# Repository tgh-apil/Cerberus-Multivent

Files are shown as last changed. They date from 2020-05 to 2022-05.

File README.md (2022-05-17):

# Cerberus-Multivent
A system using standard ventilation circuit parts and localy-manufacturable custom components to allow the use of a single ventilator to support multiple patients.

The system allows **independent control of tidal volume, FiO2, and PEEP for each patient**. 

The sub-circuit for each patient is pressure isolated and separated by N99 filters from main ventilator. There is no theoretical limit on the number of secondary circuits possible. The effective limitations are physical space for patients and the maximum tidal volume and pressure deliverable by the primary ventilator.

Supports pressure-limited volume control ventilation only. Patients must be deeply sedated with minimal spontaneous respitory activity.

Cerberus-Multivent is an open-source medical device project managed by the [Lynn and Arnold Irwin Advanced Perioperative Imaging Lab](https://apil.ca) at Toronto General Hospital, University Health Network.

# DISCLAIMER
This is an **INVESTIGATIONAL MEDICAL DEVICE** being evaluated for use
in hospital setting during **extreme crisis** leading to ventilator
shortages.

It has **not been approved** by any regulatory body.

Its use is **not endorsed** by any institution or professional body,
including the ones where it was developed and tested.

We have made every effort to make the system as safe as possible and to
provide documentation and educational materials for its use, should it be
necessary, in order to minimize the very significant risks of iatrogenic harm.

Any clinical application requires close monitoring of patients by automated 
systems and living, breathing care providers familiar with the system and its 
hazards.

It is posted here in order to facilitate rapid knowledge sharing and research
on strategies for addressing the global ventilator shortages.

Any of use of this device is done purely at your own risk and liability. The
developers and associated institutions do not accept any liability for its use.

# Publications & Media
1. <a href="https://journals.lww.com/ccejournal/Fulltext/2020/05000/Personalized_Ventilation_to_Multiple_Patients.3.aspx?context=LatestArticles" rel="nofollow" target="_blank">Han JS, Mashari A, Singh D, Dianti J, Goligher E, Long M, Ng W, Wasowicz M, Preiss D, Vesely A, Kacmarek R, Keshavjee S, Brochard L, Fisher JA, Slutsky AS. Personalized Ventilation to Multiple Patients Using a Single Ventilator: Description and Proof of Concept. Critical Care Explorations. 2020 May;2(5):e0118.</a>
2. <a href="https://www.cbc.ca/listen/live-radio/1-193-fresh-air/clip/15775663-how-a-doctor-used-his-mentors-30-year-old-paper-to-make-a-split-ventilator-for-two-people" rel="nofollow" target="_blank">How a doctor used his mentor’s 30-year-old paper to make a split ventilator for two people. Fresh Air with Nana aba Duncan. Toronto: Canadian Broadcasting Corporation; 2020.</a>

# Documentation
Cerberus was originally designed to allow complete assembly using commercial off-the-shelf (COTS) ventilator circuit components. In addition to this original version, we created two custom components to make the system more robust and allow the adjustment of PEEP for each patient. Custom component design files can be found in the repository.

## Bill of Materials & Assembly Instructions:

1. <a href="https://github.com/tgh-apil/Cerberus-Multivent/blob/master/Documentation/Cerberus%20-%20BOM%20and%20Assembly%20Instructions%20-%20Hospital%20COTS%20Components.pdf" rel="nofollow" target="_blank">BOM and Assembly Instructions (COTS version)</a>

2. <a href="https://github.com/tgh-apil/Cerberus-Multivent/blob/master/Documentation/Cerberus%20-%20BOM%20and%20Assembly%20Instructions%20-%20Micromanufactured%20Components.pdf" rel="nofollow" target="_blank">BOM and Assembly Instructions (With customized components)</a>

## Instructions for Use

1. <a href="https://github.com/tgh-apil/Cerberus-Multivent/blob/master/Documentation/Cerberus%20-%20Safety%20Check%20Lists.pdf" rel="nofollow" target="_blank">Safety Check Lists</a> 

2. <a href="https://github.com/tgh-apil/Cerberus-Multivent/blob/master/Documentation/Cerberus%20-%20Quick%20Guide.pdf" rel="nofollow" target="_blank">Quick Guide</a> 

## Mathematical Model & Simulator

A mathematical model of the system along with a simulator have been created for staff training. The simulator includes a solver that suggests settings to achieve specific end points. All software is in beta. Software is for educational and research use only.

1. <a href="https://github.com/tgh-apil/Cerberus-Multivent/tree/master/Simulator" rel="nofollow" target="_blank">Mathematical Model</a>

2. <a href="https://ventilator-simulator.now.sh/" rel="nofollow" target="_blank">Simulator</a>  

Developed by Azad Mashari, Eitan Grinspun, Bai Li, Isaac Waller, Jim Duffin, Devin Singh

# Cerberus-multivent: System Description

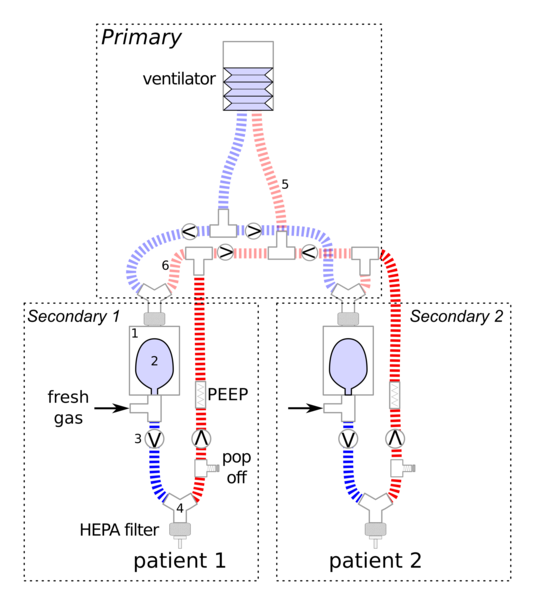
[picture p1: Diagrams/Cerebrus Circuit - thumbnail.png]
Cerberus Schematic


One suggested approach to the severe global shortage of ventilators during the current pandemic has been the splitting of ventilators in order to ventilate multiple patients with one device. The simplest version of this involves simply splitting the inspiratory and expiratory limbs of the circuit into a branch for each patient. Indeed a 3D-printable splitter device, the Prisma VEsper, was granted emergency approval by the FDA last week. This approach however poses significant risks and has a high likelihood of harming one or both patients. This motivated a joint statement by all the major critical
care and related societies (<a href="https://www.apsf.org/news-updates/joint-statement-on-multiple-patients-per-ventilator" rel="nofollow" target="_blank">https://www.apsf.org/news-updates/joint-statement-on-multiple-patients-per-ventilator</a>) warning about the hazards of such an approach.

Cerberus, named for the multi-headed dog of Greek mythology, is a ventilator splitting system that allows largely independent ventilation settings for the co-ventilated patients.

The primary ventilator works to drive multiple bellows assemblies, one for each patient. Each patient has a separate fresh gas flows and pressure-isolated secondary circuit.

On inspiration, the inspiratory pressure generated by the ventilator is Y split with one arm per patient. The gas flow from each of these arms drives a bellows assembly (consisting of reservoir bag inside a canister) uniquely connected to the inspiratory limb of each patient circuit. These also include fresh gas inlets for each patient. There is no sharing of inspiratory gas streams. Each patient receives customized fresh gas mix from an unshared source. During expiration the fresh gas flow refills the reservoir bag for the next breath. The expiratory limbs for each patient include an in-line PEEP valve and converge, along with the drive gas outflow from the bellows assemblies into the expiratory limb of the primary circuit. Check valves and filers are placed to pressure isolate all patient circuits and mitigate risk of infections transmission among patients.

# Development Team &amp; Collaborators

The Cerberus multi-vent is based on a design first presented by Sommer, Fisher et al. **Sommer DD, Fisher JA, Ramcharan V, Marshall S, Vidic DM. Improvised automatic lung ventilation for unanticipated emergencies. Crit Care Med. 1994;22: 705–709.** You can find a personal account from Dr. Joe Fisher of how the project came about <a href="https://www.drjoefisher.com/posts/fresh-air-cbc-may-9-2020-covid-19-and-the-real-back-story" rel="nofollow" target="_blank">here</a> 

**Core Development Team**: Jay Han, Devin Singh, Joseph Fisher, and Azad Mashari, From the Department of Anesthesia and Pain Management, Toronto General Hospital, University Health Network.

**Review & Evaluation**: Jose Dianti, Ewan Goligher, Michael Long, William Ng, Marcin Wasowicz, David Priess, Alex Vesely, Arnaud Mbadjeu, Robert Kacmarek, Shaf Keshavjee, Maha Al-Mandhari, Jesse May, Laurent Brochard, and Arthur Slutsky, from the Departments of Anesthesiology and Pain Management, Critical Care Medicine, Respiratory Care, Surgery and Medicine at University Health Network & St. Michaels Hospital, Toronto; Hospital Italiano de Buenos Aires, Argentina; Brigham and Women’s Hospital, Boston; Surrey Memorial Hospital, Surrey. 

Development was supported by grants from the **University Health Network & Sinai Health Systems Academic Medical Organization COVID-19 Innovation Fund** and the **Toronto General & Western Hospital Foundation** at the University Health Network. This work would not have been possible without the logistical support and hundreds of hours of work from numerous collaborators including:

**UHN Medical Engineering**: Maciej Bauer, Gad Acosta, Dave Gretzinger, Ewaryst Kulikowski, Katina DiBiase

**University of Toronto Engineering / Toronto Tool Library Collaboration**: Kate Kazlovich, James Wallace, Marc Shu-Lutman, Kyle Mayers, Simon Lynch 

**UHN Department of Anesthesia and Pain Management**: Jo Carroll, Samareh Ajami

**UHN/Peter Munk Cardiac Centre,
 Lynn and Arnold Irwin Advanced Perioperative Imaging Lab**: Joshua Qua Hiansen, Vahid Anwari

**Techna Institute**: Jimmy Qiu and Team

**UHN Animal Lab**: Badru Moloo, Alyssa Goldstein, Beth Pielsticker, Sandra Lafrance and Team

**UHN Healthcare Human Factors**: Joe Cafazzo, Neil Sokol, Wayne Ho, Julie Malone

**University of Toronto Computer Science**: U of T CS Department: Eitan Grinspun, Bai Li, Isaac Waller

**UHN Infection Prevention and Control and Medical Device Reporcessing**: AnnMarie Tyson, Kathleen Ross, Alon Vaisman, Kevin Wan

**UHN Foundation**: Shauna Seabrook

**UHN Public Affairs**: Rosa Kim

Thank you!

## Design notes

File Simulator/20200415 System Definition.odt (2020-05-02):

Cerberus Simulator System Definition

2020 April 14

Note: all pressure values are gauge readings referenced to 1 atm = 0

X[i] indicated patient specific parameter X for each of two patients on the system

# 1. INPUTS

## 1.1. Patient characteristics (for each of two patients)

1.1.1. Height (H[i]): 110-200 cm

1.1.2. Weight (W[i]): 40-120 kg

1.1.3. Lung Compliance (Cr[i]): 10-70 ml/cmH20 (intervals of 5)

1.1.4. Ratio of arterial partial pressure of oxygen to fraction of inspired oxygen (PF[i]): range 100 (severe dysfunction) - 500 (Normal)

For simplicity we are combining a whole bunch of physiological parameters into one.

## 1.2. Ventilator settings

### 1. 2.1. Primary ventilator settings

1.2.1.1. Pressure Control Level (PC) : 0-70 cmH20 (intervals of 5)

1.2.1.2. Positive End-Expiratory Pressure Level (PEEP0): Should always be set to 0 and somehow *gently* highlighted. Setting this above zero is a common error.

1.2.1.3. Respiratory Rate (RR): 2-40 breaths/minute

1.2.1.4. Inspiratory Time (IT): 0.5-(0.6/RR) s (That is inspiration should be no more than 60% of the respiratory cycle)

1.2.1.5. Inspiratory Time:Expiratory Time Ratio (IER): Discrete: 1.5:1 ; 1:1 ; 1:2 ; 1:3 (This represents the same info at IT but in a different form that will be more familiar for some users. For simplicity we can make this adjustable and make IT automatically calculated and displayed next to it. [ I:E = IT:((1/RR)-IT) ]

### 1.2.2. Secondary circuits settings (for each of two secondary circuits

1.2.2.1. Fresh Gas Oxygen Flow (FGFO[i]): 0-15 LPM (intervals of 1 for all flow variables)

1.2.2.2. Fresh Gas Air Flow (FGFA[i]): 0-15LPM

1.2.2.3. PEEP Valve Setting (PEEP[i]): 0-25 cmH20

# 2. Outputs

(values outside normal range should be highlighted)

## 2.1. Patient Arterial Blood Gas Analysis (for each patient)

2.1.1. pH[i]: Normal 7.3-7.4. Function of PaCO2[i] and HCO3[i];

- [H+] nM/L = 24 * PaCO2 (mmHg)/[HCO3] mM/L
- pH = -log10[H+]

2.1.2. Partial pressure of carbon dioxide (PaCO2[i]): N 35-45 mmHg (note different pressure units from above pressure values)

- Function of minute alveolar ventilation (3.1) and CO2 Production (3.2).
- We can assume that expired gas has similar CO2 partial pressure to the arterial gas, so
- MAV[i]*PaCO2[i] = CO2P[i] (unit conversions needed)

2.1.3. Partial pressure of oxygen (PaO2[i]): N > 100 mmHg PO2 = FiO2 * PaO2:FiO2

2.1.4. Bicarbonate concentration (HCO3[i]): N 22-28 mEq/L

## 2.2. Ventilator derived values (for each patient)

2.2.1. Peak Inspiratory pressure (PIP[i]): range 0-40 cm H2O; note: circuit includes a pop-off valve at 40 so pressure can never go above that

2.2.2. Actual PEEP (APEEP[i]): cm H2O

- Total fresh gas flow: FGFTot[i] = FGFO[i] + FGFA[i] (air + oxygen)
- Intrinsic PEEP (from FGF): PEEPInt[i] = 0 if FGFtot[i] < 7LPM; 3 + (FGFtot[i] – 7)*0.6
- APEEP[i] = PEEP0 + PEEPInt[i] + PEEP[i]

2.2.3. Tidal volume (VT[i]): 50-700 ml (Normal range depends on weight: 4-8 ml/kg) = 0.5x PIP x Cr for each patient (mean inspiratory pressure assumed to be half of PIP)

2.2.4. Fraction Inspired Oxygen (FiO2[i]): (FGFA*0.21 + FGFO) / (FGFA + FGFO)

# 3. Hidden Variables

## 3.1 Minute alveolar ventilation

3.1.1 Anatomical Dead Space ADS[i] = W[i]/0.45 ml

3.1.2 Secondary Circuit compliance CC[i] = constat CC for simplicity

3.1.3 Alveolar Tidal Volume AVT[i] = VT[i] – ( PIP[i] / 2*CC ) - ADS[i]

approx. assumes linear increase in pressure

3.1.4 Minute Alveolar Ventilation MAV[i] = RR*AVT[i]

3.2 CO2 production rate (VCO2[i]) = 0.4 + (Weight kg / 70 kg ) * 0.2 g / min (I more or less made this up; average value for 70kg adult is around 0.6 g/min and it varies with weight; for our purposes and the range of adult weights, we are considering that equation is probably good enough

# References

Kassirer JP, Bleich HL. Rapid Estimation of Plasma Carbon Dioxide Tension from pH and Total Carbon Dioxide Content. New England Journal of Medicine. 1965;272: 1067–1068. doi:10.1056/NEJM196505202722007 (https://doi.org/10.1056/NEJM196505202722007)

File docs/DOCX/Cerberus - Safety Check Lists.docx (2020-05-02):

Step 1: Driving Circuit Leak Test
Setup: a) Connect the inspiratory and expiratory limbs of the Cerebrus system to the corresponding inspiratory and expiratory ports of the driving ventilator b) Occlude the patient Y of each secondary circuit | Performance: I. Perform a standard low P leak test using an anesthetic gas machine | PASS - Leak < 500 mL

Step 2: Secondary Circuit Leak Test
Setup: a) Connect test lungs to the end of each secondary circuit* b) Set driving ventilator to initial system setup up parameters c) Begin ventilation on test lungs * Anesthetic gas machine (AGM) breathing bags can be used as test lungs* | Performance I. Allow the test lungs inflate and deflate II. Allow 2 minutes of ventilation III. Note the total volume returned to the ventilator IV. Allow the lungs to ventilate for an additional 2 minutes | PASS - Each test lung visually inflates and deflates with each respiratory cycle of the driving ventilator - Volume return to the ventilator remains constant for 2 minutes after the total volume was noted

Step 3: Fresh Gas Flow Check
Setup: a) Ensure the fresh gas flows to each secondary circuit is attached b) Set each fresh gas flow to 4 L/min | Performance I. With each fresh gas flow set to 4 L/min allow 2 minutes of ventilation II. After 2 minutes note the total volume returned to the ventilator III. Change the fresh gas flow on Lung A to 10 L/min while holding lung B at 4 L/min IV. Ventilate for 2 minutes V. Note the total volume returned to the ventilator VI. Note any change in the observed inflation in Lung A VII. Return fresh gas flow on Lung A to 4 L/min VIII. Repeat steps (III – VII) with lung B set to 10 L/min and lung A held at 4 L/min | PASS (all conditions must be met) - breath-delivery bag inflates and deflates with each respiratory cycle of the driving ventilator - Increased volume returned to driving ventilator AND increased lung expansion of Lung A following Step VI - Increased volume returned to driving ventilator AND increased lung inflation of Lung B following Step VIII

Step 4: Secondary Circuit Independence
Setup: a) Set driving ventilator to initial system setup up parameters b) Set fresh gas flow to 4 L/min c) Begin ventilation on test lungs | Performance: I. Allow system to ventilate for 2 minutes II. Measure the tidal volume or visually observe the approximate inflation of each lung III. Decrease the compliance in Lung A IV. Ventilate for 1 min V. Measure the tidal volume lung B or visually observe the approximate inflation of Lung B VI. Return the compliance of Lung A to baseline VII. Repeat steps (III – VI) using Lung B | PASS - No major changes in measured tidal volume or observed inflation of lung B when lung A compliance is decreased AND - No major changes in measured tidal volumes or observed inflation of lung A when lung B compliance is decreased

Step 5: Manometer Check
Setup: a) Set driving ventilator to initial system setup parameters b) Ensure manometer is installed into the sampling port of the HME filter distal to the patient Y c) Ensure each secondary circuit is attached to a test lung d) Ensure the PEEP valves on each secondary expiratory limb is set to 5 cm H2O e) Set fresh gas flow rates for each secondary circuit is set to 4 L/min | Performance: I. Note the nadir (lowest reading) on the manometer II. Note the zenith (highest reading) on the manometer | PASS - Zenith (peak inspiratory pressure) occurs with each inspiration - Peak inspiratory pressure does not equal the driving pressure of the ventilator - Nadir occurs at end expiration (PEEP) and the manometer reads at least 5 cm H2O* *PEEP may be higher than 5 cm H2O due to intrinsic PEEP generated by the constant fresh gas flow. Higher fresh gas flow rates lead to higher intrinsic PEEP*

Step 6: Disconnect Alarm
Setup: a) Set driving ventilator to initial system setup up parameters b) Set fresh gas flow to 4 L/min for each secondary circuit c) Begin ventilation on test lungs | Performance: I. Allow lungs to ventilate for 2 minutes to reach steady state II. Set volume alarms according to instructions on ALARM SETTING III. Disconnect Lung A IV. Reconnect Lung A V. Disconnect Lung B VI. Reconnect Lung B | PASS - Disconnect of Lung A results in low volume alarm AND - Disconnect of Lung B results in low volume alarm

Step 7: Pop-Off Valve Integrity AND Occlusion Alarm
Setup: a) Set driving ventilator to initial system setup up parameters b) Set fresh gas flow to 8 L/min for each secondary circuit c) Begin ventilation on test lungs | Performance: I. Allow lungs to ventilate for 2 minutes to reach steady state II. Set volume alarms according to instructions on “Alarm Settings” III. Clamp Lung A distal to secondary circuit Y IV. Note peak pressure on Lung A as measured by inline manometer V. Unclamp Lung A VI. Allow lungs to ventilate until volume alarm ceases VII. Clamp Lung B distal to secondary circuit Y VIII. Note peak pressure on Lung B as measured by inline manometer IX. Unclamp Lung A X. Allow lungs to ventilate until volume alarm ceases | PASS - Clamping of Lung A results in: - Low volume alarm - Peak inspiratory pressure as measured by inline manometer = 45 cm H2O AND - Clamping of Lung B results in: - Low volume alarm - Peak inspiratory pressure as measured by inline manometer = 45 cm H2O

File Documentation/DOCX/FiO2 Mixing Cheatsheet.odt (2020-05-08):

Total Flow (L/min) | 100% Oxygen (L/min) | Medical air (L/min) | FiO2
4 | 4 | 0 | 1.00
| 3 | 1 | 0.80
| 2 | 2 | 0.61
| 1 | 3 | 0.41
| 0 | 4 | 0.21
5 | 5 | 0 | 1.00
| 4 | 1 | 0.84
| 3 | 2 | 0.68
| 2 | 3 | 0.53
| 1 | 4 | 0.37
| 0 | 5 | 0.21
6 | 6 | 0 | 1.00
| 5 | 1 | 0.87
| 4 | 2 | 0.74
| 3 | 3 | 0.61
| 2 | 4 | 0.47
| 1 | 5 | 0.34
| 0 | 6 | 0.21
7 | 7 | 0 | 1.00
| 6 | 1 | 0.89
| 5 | 2 | 0.77
| 4 | 3 | 0.66
| 3 | 4 | 0.55
| 2 | 5 | 0.44
| 1 | 6 | 0.32
| 0 | 7 | 0.21
8 | 8 | 0 | 1.00
| 7 | 1 | 0.90
| 6 | 2 | 0.80
| 5 | 3 | 0.70
| 4 | 4 | 0.61
| 3 | 5 | 0.51
| 2 | 6 | 0.41
| 1 | 7 | 0.31
| 0 | 8 | 0.21
9 | 9 | 0 | 1.00
| 8 | 1 | 0.91
| 7 | 2 | 0.82
| 6 | 3 | 0.74
| 5 | 4 | 0.65
| 4 | 5 | 0.56
| 3 | 6 | 0.47
| 2 | 7 | 0.39
| 1 | 8 | 0.30
| 0 | 9 | 0.21

Total Flow (L/min) | 100% Oxygen (L/min) | Medical air (L/min) | FiO2
10 | 10 | 0 | 1.00
| 9 | 1 | 0.92
| 8 | 2 | 0.84
| 7 | 3 | 0.76
| 6 | 4 | 0.68
| 5 | 5 | 0.61
| 4 | 6 | 0.53
| 3 | 7 | 0.45
| 2 | 8 | 0.37
| 1 | 9 | 0.29
| 0 | 10 | 0.21
11 | 11 | 0 | 1.00
| 10 | 1 | 0.93
| 9 | 2 | 0.86
| 8 | 3 | 0.78
| 7 | 4 | 0.71
| 6 | 5 | 0.64
| 5 | 6 | 0.57
| 4 | 7 | 0.50
| 3 | 8 | 0.43
| 2 | 9 | 0.35
| 1 | 10 | 0.28
| 0 | 11 | 0.21
12 | 12 | 0 | 1.00
| 11 | 1 | 0.93
| 10 | 2 | 0.87
| 9 | 3 | 0.80
| 8 | 4 | 0.74
| 7 | 5 | 0.67
| 6 | 6 | 0.61
| 5 | 7 | 0.54
| 4 | 8 | 0.47
| 3 | 9 | 0.41
| 2 | 10 | 0.34
| 1 | 11 | 0.28
| 0 | 12 | 0.21

Total Flow (L/min) | 100% Oxygen (L/min) | Medical air (L/min) | FiO2
13 | 13 | 0 | 1.00
| 12 | 1 | 0.94
| 11 | 2 | 0.88
| 10 | 3 | 0.82
| 9 | 4 | 0.76
| 8 | 5 | 0.70
| 7 | 6 | 0.64
| 6 | 7 | 0.57
| 5 | 8 | 0.51
| 4 | 9 | 0.45
| 3 | 10 | 0.39
| 2 | 11 | 0.33
| 1 | 12 | 0.27
| 0 | 13 | 0.21
14 | 14 | 0 | 1.00
| 13 | 1 | 0.94
| 12 | 2 | 0.89
| 11 | 3 | 0.83
| 10 | 4 | 0.77
| 9 | 5 | 0.72
| 8 | 6 | 0.66
| 7 | 7 | 0.61
| 6 | 8 | 0.55
| 5 | 9 | 0.49
| 4 | 10 | 0.44
| 3 | 11 | 0.38
| 2 | 12 | 0.32
| 1 | 13 | 0.27
| 0 | 14 | 0.21

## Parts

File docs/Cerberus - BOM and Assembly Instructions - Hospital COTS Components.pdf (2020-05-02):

Equipment and Supplies (needed to prepare vent sharing between TWO (2) patients) Specific equipment required may vary depending on supplies and equipment availability

### 1. One (1) ventilator (driving ventilator) 2. Two (2) sets of patient tubing (inspiratory = blue, expiratory = white) 3. Four (4) short circuit tubings

a. Ideally two (2) pairs of distinctly different tubing colours (two (2) clear tubings and two (2) blue tubings)

### 4. Four (4) t-piece connectors (often used in spontaneous breathing trials) 5. Eight (8) 22 mm to 22 mm connectors 6. Six (6) 15 mm to 15 mm connectors

7. Four (4) y-connectors (normally used for connection of patient endotracheal tube to ventilator)

### 8. Eight (8) one-way valves (to be connected in-line) 9. Two (2) 1.5-2 L suction cannisters with corresponding lids

a. Cannister requirements
i. Lids must have at least two (2) communicating openings.
- One port must be able to connect the single end of a standard Y-connector to the cannister
- One port must be able to connect both the standard ventilator tubing on the external side of the lid and the breathing bag on the internal side of the cannister lid.
- This port must have a smaller secondary port on the external side of the cannister lid capable of connecting fresh gas supply
b. Ideally, the lid closes onto cannister with threaded connection. This cannister is pressurized and the lid must be prevented from leaking or being lifted up. If press fit, the lids must also be glued to the cannister. Glue (methyl methacrylate) can be used as gas from the cannister does NOT reach the patient.
10. Two (2) 1 litre anesthesia breathing bags (used to ventilate patients in circle system ventilators)

### 11. Two (2) silicone connectors 12. Two (2) Gas Sample Tee adapters 13. Two (2) 11.0 mm endotracheal tube (ETT) connectors

a. Can be found on 41 Fr Mallinckrodt double lumen ETT

### 14. Two (2) antimicrobial / heat and moisture exchangers (HMEs) 15. Two (2) elbow connectors (optional) 16. Two (2) manometers 17. Two (2) fresh gas flow lines

Note: Combined HME + antimicrobial filters are recommended if available. If unavailable, then one could use separate antimicrobial and HME filters. The filter must be placed between the patient Y and the ETT tube in order to filter the gas that is both inspired to and expired from the patient.

Images of required equipment

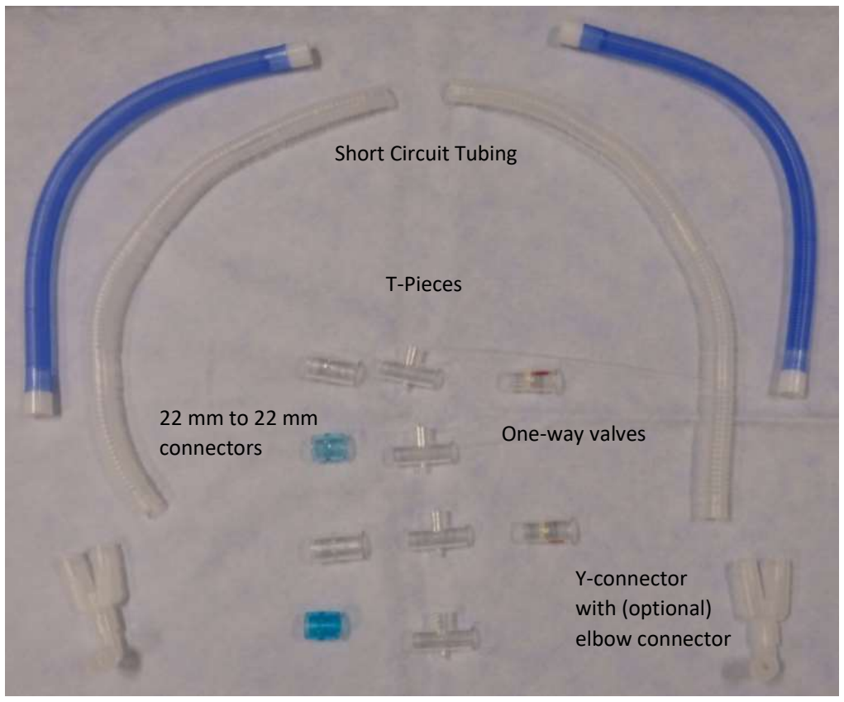
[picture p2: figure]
Short Circuit Tubing; T-Pieces; 22 mm to 22 mm connectors; One-way valves; Y-connector with (optional) elbow connector

### 2 L suction

cannister
and lid

Silicone
Connector

Breathing Bag 15 mm to 15 mm connector

Gas Sample Tee
adapters

ETT
connector

HME +
Antimicrobial
filter

PEEP valve
with connector
(2 options)

Patient Tubing

Manometer

### Cerberus System Schematic

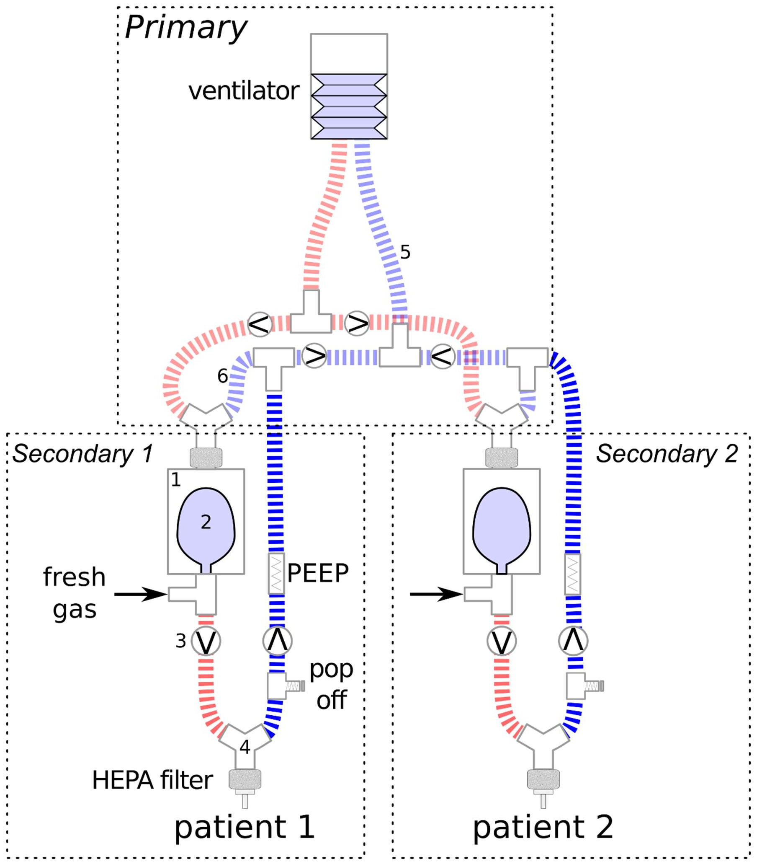
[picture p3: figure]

### Setting up the ventilator for two-patient ventilation

Creation of the “Driving Circuits”
Step 1: | Connect 22 mm to 22 mm connector (blue) to bottom of one (1) t-piece

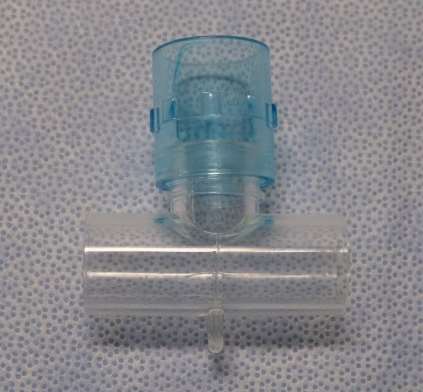
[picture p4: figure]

Step 2: | Connect short blue tubing to each open end of t-piece. This becomes the common inspiratory limb split of the ventilator (Master).

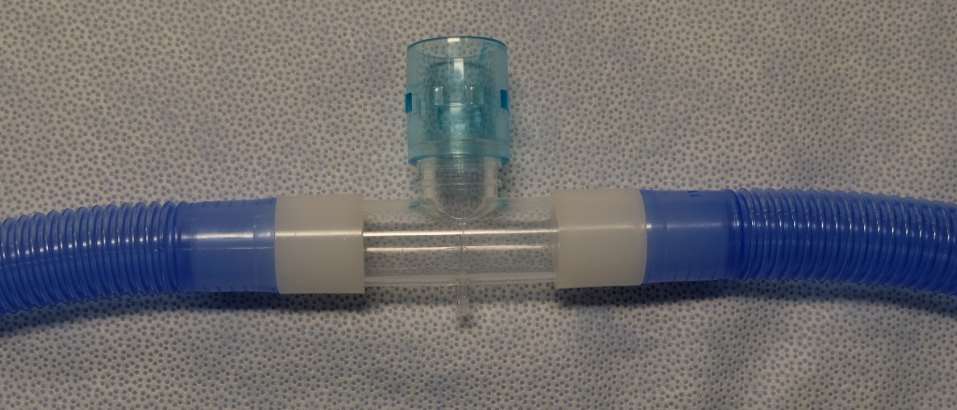
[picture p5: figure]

Step 3: | Connect the inspiratory limb t-piece (Step 2) to the common inspiratory port of the ventilator (Master) using the 22 mm to 22 mm connector previously attached (step 1) to the bottom of the t-piece.

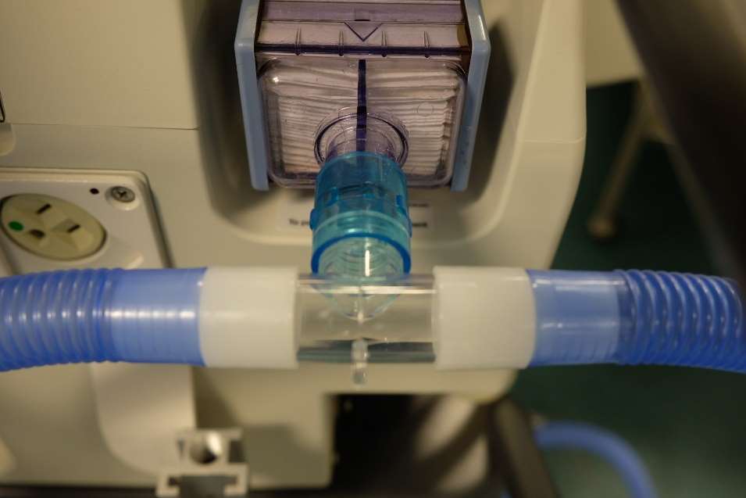
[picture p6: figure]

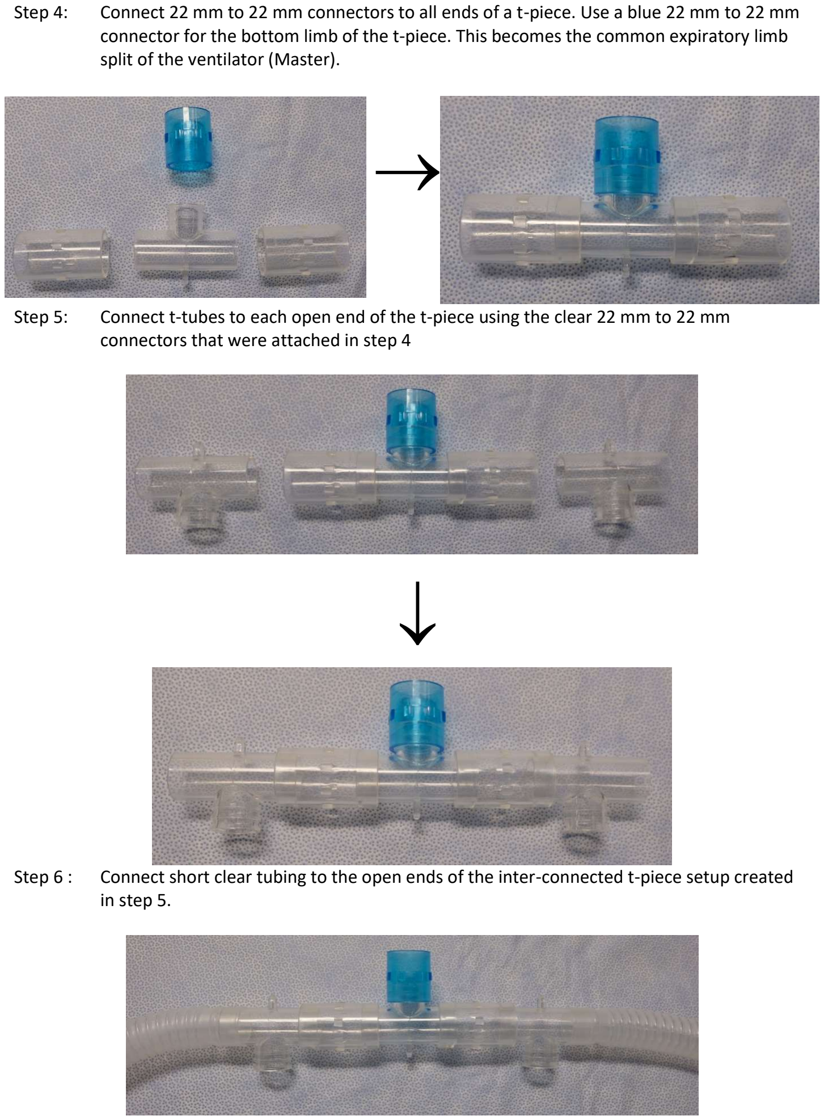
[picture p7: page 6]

Step 4: | Connect 22 mm to 22 mm connectors to all ends of a t-piece. Use a blue 22 mm to 22 mm connector for the bottom limb of the t-piece. This becomes the common expiratory limb split of the ventilator (Master).
Step 5: | Connect t-tubes to each open end of the t-piece using the clear 22 mm to 22 mm connectors that were attached in step 4
Step 6 : Connect short clear tubing to the open ends of the inter-connected t-piece setup created in step 5.

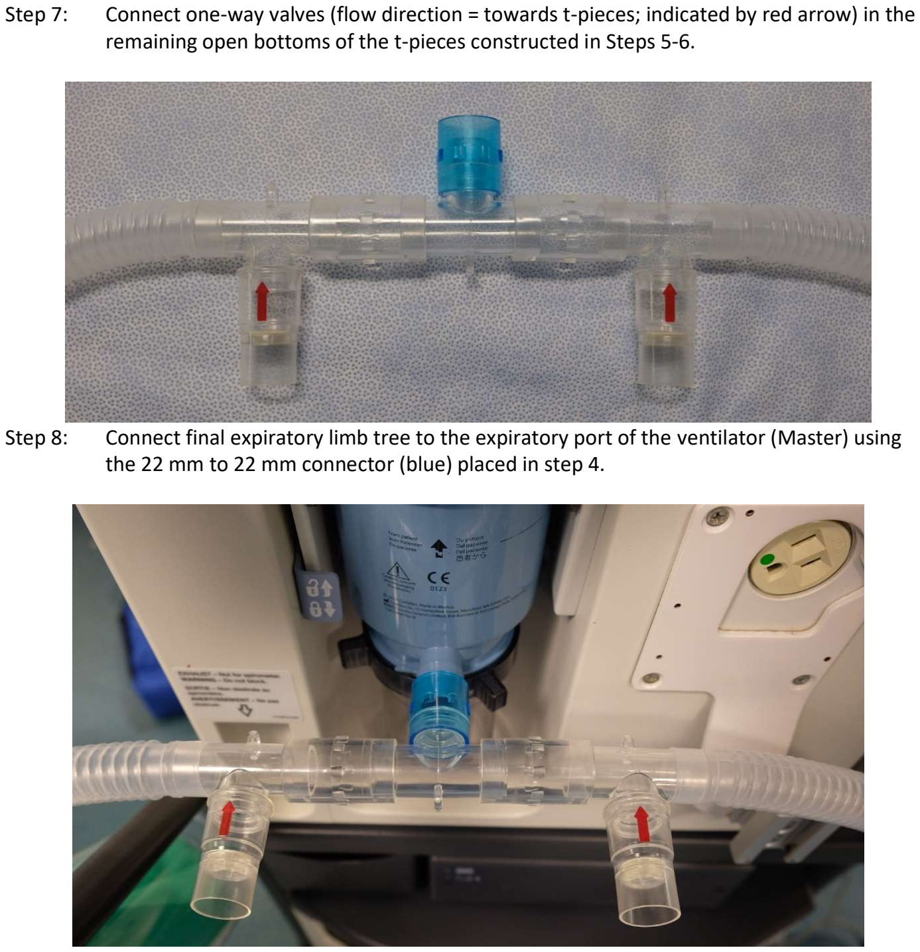
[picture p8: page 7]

Step 7: | Connect one-way valves (flow direction = towards t-pieces; indicated by red arrow) in the remaining open bottoms of the t-pieces constructed in Steps 5-6.
Step 8: | Connect final expiratory limb tree to the expiratory port of the ventilator (Master) using the 22 mm to 22 mm connector (blue) placed in step 4.

Step 9: Connect one (1) common inspiratory (short blue tubing) limb and one (1) common expiratory (short clear tubing) limb to two (2) ports of a y-connector. This creates a driving circuit for one patient.

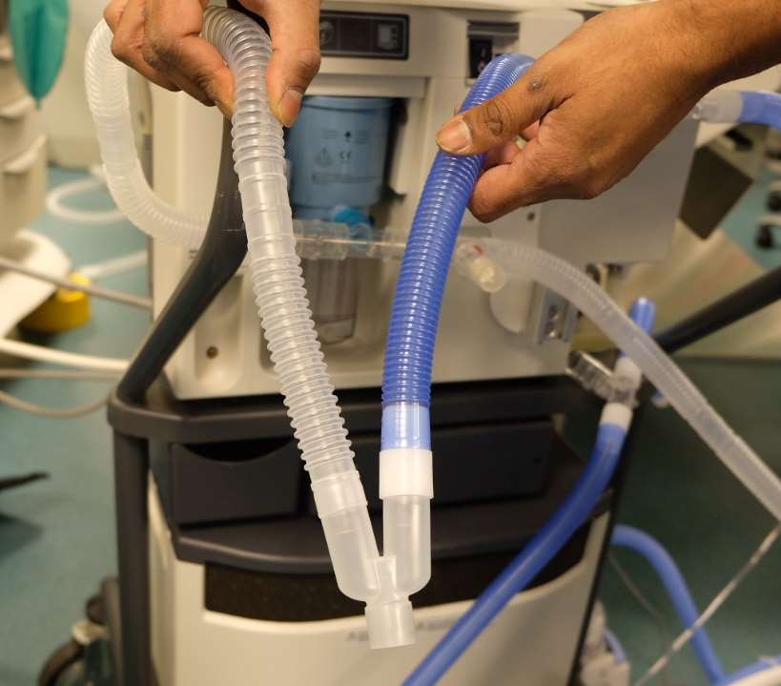
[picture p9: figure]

Step 10: Connect the remaining common inspiratory (short blue tubing) limb and common expiratory (short clear tubing) limbs of the driving circuit to two (2) ports of a y-connector. This creates the second driving circuit.


Construction of “Bag-in-a-bottle” **
Step 11: Use a 15 mm to 15 mm connector to connect the 1 L breathing bag to the silicone connector.
Step 12: Cut down the silicon connector so that it is flush with the 15 mm to 15 mm connector.

Step 13: Insert the silicone connector through the largest opening of the suction cannister lid so that bag is on the underside of the lid. Ensure that the silicone connector is flush with the exterior surface of the lid.
- In order to facilitate insertion of the silicone connector we recommend coating the exterior with an alcohol wipe before rapidly inserting the connector into the opening.


Step 14: Connect a 11.0 mm ETT connector to the tapered opening of the suction cannister lid.
- Once firm connection is established it is advisable to glue/epoxy the ETT connector to the cannister.


Step 15: Connect gas sample tee to the 15 mm port embedded in the silicone connector.


Step 16: Seal any additional openings on the suction cannister lid.
Step 17: Attach suction cannister lid to cannister. Seal lid to cannister using epoxy/glue.
- Ideally, test seal to a pressure of at least 150 cm of water.



Creation of “Individual” patient circuits
Step 18: Connect one-way valve (direction of flow = away from cannister; indicated by blue arrow) to the open end of the gas sample tee using a 22 mm to 22 mm connector.
Step 19: Connect the other end of one-way valve to the proximal inspiratory limb (blue tubing) of the patient tubing using a 15mm to 15 mm connector.
Step 20: Connect a one-way valve (direction of flow = towards patient; indicated by blue arrow) to the distal end of the of the inspiratory limb (blue tubing).


Step 21: Connect the distal end of the inspiratory limb with one-way valve in place to one (1) port of a y- connector.
Step 22: Connect a one-way valve (direction of flow = away from patient; indicated by red arrow) to the distal end of the expiratory limb (white tubing) of the patient circuit using a 15 mm to 15 mm connector.


Step 23: Connect the distal end of the expiratory limb (white tubing) with one-way valve in place to the other port of the y-connector using a 22 mm to 22 mm connector.
Step 24: place HME filter on distal port of y-connector immediately proximal to patient endotracheal tube.


Step 25: Install manometer into the gas sampling port of the HME filter
- Optionally, pressure tubing can be placed can be used to connect the manometer to the gas sampling port allowing one to extend the placement of the manometer. (as depicted)
Step 26: Connect the proximal end of the expiratory limb of patient circuit to one of the one-way valves (Step 7) found on the common expiratory tree.

Step 27: Repeat steps 11-26 for second patient circuit.
Step 28: Attach a two-limbed driving circuit (short blue and short clear tubings) that is y-connected to the ETT connector of the suction cannister. One driving circuit per cannister.
- Elbows are optionally placed between Y-connector and suction cannister ETT connector.


Step 29: Connect fresh gas flow to the sampling port of the gas sample tee adapter.
- Independent fresh gas flow is required for each patient circuit
- Recommended to permanently fix the fresh gas flow line to the gas sample tee in order to minimize risk of disconnection.


How to add independent PEEP to a patient circuit
PEEP insertion: | Insert the PEEP valve between the one-way valve located at the proximal end of
| the patient circuit and the common expiratory tree.
| PEEP valves with directed vented gas must be used in order to vent any
| escaping flow back to the common expiratory tree.
| A minimum PEEP valve of 5 cm H2O required in each secondary circuit
| expiratory limb


NOTE: PEEP valve depicted cannot be substituted for more familiar mushroom valve PEEP systems seen on BMV setups unless custom casing is used. See alternate instructions for details of custom casing
- PEEP exhaust must be given back to the common expiratory port of the driving ventilator to satisfy the ventilator’s volume detection

Cerberus System – Physical Circuit
- Connect common Inspiratory Limb into inspiratory port of driving ventilator
- Connect common Expiratory Limb tree into expiratory port of driving ventilator

Connection to driving ventilator inspiratory port

Connection to driving ventilator expiratory port


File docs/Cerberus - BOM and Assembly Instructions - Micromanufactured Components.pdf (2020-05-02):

Equipment and Supplies (needed to prepare vent sharing between TWO (2) patients) Specific equipment required may vary depending on supplies and equipment availability

### 1. One (1) ventilator (Master) 2. Two (2) sets up patient tubing (inspiratory = blue, expiratory = white) 3. Four (4) short circuit tubings

a. Ideally two (2) pairs of distinctly different tubing colours (two (2) clear tubings and two
(2) blue tubings)

### 4. Five (5) t-piece connectors (often used in spontaneous breathing trials) 5. Six (6) 22 mm to 22 mm connectors 6. Four (4) 15 mm to 15 mm connectors

7. Four (4) y-connectors (normally used for connection of patient endotracheal tube to ventilator)

### 8. Eight (8) one-way valves (to be connected in-line) 9. One (1) 1.5 – 2 L container with threaded flat top lid 10. One (1) 3D printer connection system

11. Two (2) 1 litre anesthesia breathing bags (used to ventilate patients in circle system ventilators)

### 12. Two (2) antimicrobial / heat and moisture exchangers (HMEs) 13. Two (2) manometers 14. Two (2) fresh gas flow lines 15. Two (2) adjustable PEEP valves (used in BMV circuits) 16. Two (2) Intersurgical™ APL valves (0-60 cm H2O)

Note: Combined HME + antimicrobial filters are recommended if available. If unavailable, then one could use separate antimicrobial and HME filters. The filter must be placed between the patient Y and the ETT tube in order to filter the gas that is both inspired to and expired from the patient.

Images of required equipment

Short Circuit Tubing; T-Pieces; 22 mm to 22 mm connectors; One-way valves; Y-connector with (optional) elbow connector

### 1.5 L

container
with
threaded lid

Breathing
Bag

3D connection system
and O ring

HME +
Antimicrobial
filter

Patient Tubing

PEEP valve
with connector
(2 options)

Manometer

### Cerberus System Schematic


### Setting up the ventilator for two-patient ventilation

Creation of the “Driving Circuits”
Step 1: | Connect 22 mm to 22 mm connector (blue) to bottom of one (1) t-piece
Step 2: | Connect short blue tubing to each open end of t-piece. This becomes the common inspiratory limb split of the ventilator (Master).


Step 3: | Connect the inspiratory limb t-piece (Step 2) to the common inspiratory port of the ventilator (Master) using the 22 mm to 22 mm connector previously attached (step 1) to the bottom of the t-piece.



Step 4: | Connect 22 mm to 22 mm connectors to all ends of a t-piece. Use a blue 22 mm to 22 mm connector for the bottom limb of the t-piece. This becomes the common expiratory limb split of the ventilator (Master).
Step 5: | Connect t-tubes to each open end of the t-piece using the clear 22 mm to 22 mm connectors that were attached in step 4
Step 6: | Connect short clear tubing to the open ends of the inter-connected t-piece setup created in step 5.


Step 7: | Connect one-way valves (flow direction = towards t-pieces; indicated by red arrow) in the remaining open bottoms of the t-pieces constructed in Steps 5-6.
Step 8: | Connect final expiratory limb tree to the expiratory port of the ventilator (Master) using the 22 mm to 22 mm connector (blue) placed in step 4.

Step 9: | Connect one (1) common inspiratory (short blue tubing) limb and one (1) common expiratory (short clear tubing) limb to two (2) ports of a y-connector. This creates a driving circuit for one patient.


Step 10: | Connect the remaining common inspiratory (short blue tubing) limb and common expiratory (short clear tubing) limbs of the driving circuit to two (2) ports of a y- connector. This creates the second driving circuit.


Construction of “Bag in a bottle”
Step 11: | Cut hole of appropriate size into threaded lid (indicated by black shading)
| Our custom design uses a hole of diameter = 50 mm
Step 12: | Create 3D connection system with two primary communicating ports that will be exterior to the cannister and one port that will sit inside the sealed container. Smaller primary exterior port has an outer diameter = 15 mm (fits standard ETT elbow connector). Larger primary exterior port has an inner diameter = 22 mm. This port is continuous with the interior port which has an outside diameter 21 mm. o This larger primary exterior port requires a secondary inlet with an outside diameter = 6.5 mm
| See end of instructions for engineering specifications


Step 13: | Attach 3D connection system to lid using the 50 mm hole created in Step 11 O ring sits between threaded washer and internal surface of lid.
Step 14: | Connect 1 L breathing bag to the port located on the internal side of the lid


Step 15: | Place breathing bag inside bottle and close lid In order to increase seal of bottle, one can add plumber’s tape/self-fusing tape to the threads located on the glass bottle
Step 16: | Circumferentially seal the 3D printed connection system to the exterior surface of the lid. Any sealant can be used. We have used cyanoacrylate (Krazy Glue™/Gorilla Glue™)

Step 17: Circumferentially tape the smaller primary exterior port Use synthetic material such as electrical tape This tape provides a smooth surface to facilitate a tight seal at this component. The 3D material is roughened and will leak otherwise.


Creation of “Individual” patient circuits
Step 18: | Connect one-way valve (direction of flow = away from cannister; indicated by blue
| arrow) to the larger primary port of completed “bag-in-a-bottle”


Step 19: | Connect the other end of one-way valve to the proximal inspiratory limb (blue tubing) of the patient tubing using a 15mm to 15 mm connector.
Step 20: | Connect a one-way valve (direction of flow = towards patient; indicated by blue arrow) to the distal end of the of the inspiratory limb (blue tubing).


Step 21: | Connect the distal end of the inspiratory limb with one-way valve in place to one (1) port of a y- connector.
Step 22: | Connect a one-way valve (direction of flow = away from patient; indicated by red arrow) to the distal end of the expiratory limb (white tubing) of the patient circuit using a 15 mm to 15 mm connector.


Step 23: | Connect the distal end of the expiratory limb (white tubing) with one-way valve in place to the other port of the y-connector using a 22 mm to 22 mm connector.
Step 24: | place HME filter on distal port of y-connector immediately proximal to patient endotracheal tube.


Step 25: | Install manometer into the gas sampling port of the HME filter Optionally, pressure tubing can be placed can be used to connect the manometer to the gas sampling port allowing one to extend the placement of the manometer
Step 26: | Connect the proximal end of the expiratory limb of patient circuit to one of the one- way valves (Step 7) found on the common expiratory tree.


Step 27: | Repeat steps 11-26 for the other secondary patient circuit.
Step 28: | Attach a two-limbed driving circuit (short blue and short clear tubings) that is y- connected to the ETT connector of the suction cannister. One driving circuit per cannister.
Step 29: | Connect fresh gas flow to the sampling port of the gas sample tee adapter. Independent fresh gas flow is required for each patient circuit

How to add independent PEEP to a patient circuit
PEEP insertion: | Insert the PEEP valve between the one-way valve located at the proximal end of
| the patient circuit and the common expiratory tree.
| PEEP valves with directed vented gas must be used in order to vent any
| escaping flow back to the common expiratory tree.
| A minimum PEEP valve of 5 cm H2O required in each secondary circuit expiratory
| limb


NOTE: the custom PEEP valve adapter must be used as all flow exhausted by the PEEP valve must be recaptured by the ventilator in order to satisfy the ventilator ‘s volume detection . See end of document for engineering specifications for custom design
- If custom PEEP design is not possible one must used older PEEP valves with directed outflow (see alternate instructions for image) given back to the common expiratory port of the driving ventilator

How to add pop-off valve to each secondary circuit Pop-off valve must be placed into the expiratory limb of each secondary circuit

Step 1: | Connect adjustable APL valve set to 45 cm H2O to the bottom limb of T-piece
Step 2: | Remove the proximal 15 mm to 15 mm connector between the one-way valve and the expiratory limb


Step 3: Insert t-piece with APL valve attached into the expiratory limb between one-way valve and the expiratory limb


Cerberus System – Physical Circuit
- Connect common Inspiratory Limb into inspiratory port of driving ventilator
- Connect common expiratory limb tree into expiratory port of driving ventilator

Connection to driving ventilator inspiratory port

Connection to driving ventilator expiratory port


Engineering Schematic of 3D printed connection system


O – Ring = food grade Buna-n 1/8 ‘’ width (dash number 218)

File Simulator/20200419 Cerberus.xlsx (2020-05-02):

Simple Mode Chart Display | Expert Mode Chart Display | Output Chart Group | Display Name | Input Display Group | Reference # | Variable | description | Shared Value | Value Pt 1 | Value Pt 2 | Unit | Category | Normal range | Default value
1 | 1 | Patient # | Height | 1.0.; 2.0. Patient Characteristics | 1.1.1 | H | Height |  | 140.00 | 180.00 | cm | Patient Characteristics
1 | 1 | Patient # | Weight | 1.0.; 2.0. Patient Characteristics | 1.1.2 | W | Weight |  | 55.00 | 70.00 | Kg | Patient Characteristics
1 | 1 | Patient # | Compliance | 1.0.; 2.0. Patient Characteristics | 1.1.3 | Cr | Lung Compliance |  | 15.00 | 50.00 | ml/cmH2O | Patient Characteristics
1 | 1 | Patient # | PaO2:FiO2 | 1.0.; 2.0. Patient Characteristics | 1.1.4 | PF | Arterial PaO2:FiO2 ratio |  | 100.00 | 300.00 |  | Patient Characteristics | > 300
0 | 0 |  |  |  |  | Pbar | Barometric Pressure | 760.00 |  |  | mmHg | Environmental Parameter Setting
0 | 0 |  |  |  |  | Pdry | Barometric Pressure – vapour pressure | 713.00 |  |  | mmHg | Environmental Parameter Calculated
0 | 0 |  |  |  |  | PIO2 | Partial Pressure of Inspired Oxygen in Air | 212.32 |  |  | mmHg | Environmental Parameter Calculated
1 | 1 | Primary Vent | PC | 0. Primary Ventilator Setting | 1.2.1.1 | PC | Pressure Control Level | 40.00 |  |  | cmH2O | Primary Ventilator Settings | 5-60 | 60
1 | 1 | Primary Vent | PEEP | 0. Primary Ventilator Setting | 1.2.1.2 | PEEP0 | Positive End-Expiratory Pressure Level (PEEP0): | 5.00 |  |  | cmH2O | Primary Ventilator Settings | 0 | 0 | Should always be set to 0 and somehow *gently* highlighted. Setting this above zero is a common error.
1 | 1 | Primary Vent | RR | 0. Primary Ventilator Setting | 1.2.1.3 | RR | Respiratory Rate | 18.00 |  |  | b/min | Primary Ventilator Settings | 5-35 | 15
1 | 1 | Primary Vent | I Time | 0. Primary Ventilator Setting | 1.2.1.4 | IT | Inspiratory Time (IT): 0.5 – (0.6/Ttot) s | 1.00 |  |  | s | Primary Ventilator Settings |  | Calculated based on I:E | (That is inspiration should be no more than 60% of the respiratory cycle)
1 | 1 | Primary Vent | I:E | 0. Primary Ventilator Setting | 1.2.1.5 | IER | Inspiratory Time:Expiratory Time Ratio (I:E): | 0.43 |  |  | unitless | Primary Ventilator Calculated | 2:1 – 1:4 | “1:2”
0 | 0 |  |  |  |  | VT0 | Tidal volume of primary ventilator | 500.00 |  |  | ml | Primary Ventilator Calculated |  |  | Not relevant
0 | 0 |  |  |  |  | Ttot | Duration of respiratory cycle | 3.33 |  |  | s | Primary Ventilator Calculated
0 | 1 | Secondary # | Oxygen | 1.1.; 2.1. Secondary circuit settings | 1.2.2.1 | FGFO | Fresh Gas Flow – Oxygen |  | 8.00 | 1.00 | L/min | Secondary Circuit Settings | 0-15 | 2
0 | 1 | Secondary # | Air | 1.1.; 2.1. Secondary circuit settings | 1.2.2.2 | FGFA | Fresh Gas Flow – Air |  | 2.00 | 8.00 | L/min | Secondary Circuit Settings | 0-15 | 3
1 | 1 | Secondary # | FGF Total |  |  | FGFtot | FGF Total |  | 10.00 | 9.00 | L/min | Secondary Circuit Calculated | 0-30 | 5
0 | 1 | Patient # | PIP |  | 2.2.1 | PIP | Peak Inspiratory pressure |  | 74.07 | 20.00 | cmH2O | Secondary Circuit Calculated | < 40 |  | range 0-40 cm H2O; Assumed to be twice MIP n: circuit includes a pop-of valve at 40 so pressure can never go above that; calculating this is the challenge
1 | 1 | Patient # | VT |  | 2.2.3 | VT | Patient Tidal Volume |  | 555.56 | 500.00 | ml | Secondary Circuit Calculated | 4-8 ml/kg of weight |  | This is only related to primary ventilator tidal volume when the reservoir for each patient is not completely emptied with each inspiration. When, as is most common, it is emptied, it is equivalent to the volume of the fille bag at end expiration during which time the bag is filling from the FGF.
0 | 1 | Patient # | MIP |  |  | MIP | Mean Inspiratory Pressure |  | 37.04 | 10.00 | cmH2O | Secondary Circuit Calculated
1 | 1 | Patient # | FiO2 |  | 2.2.4 | FIO2 | Fraction of Inspired Oxygen |  | 0.84 | 0.30 | unitless | Secondary Circuit Calculated
1 | 1 | Secondary # | PEEP | 1.1.; 2.1. Secondary circuit settings | 1.2.2.3 | PEEP | PEEP Valve Setting on Secondary Circuit |  | 5.00 | 5.00 | cmH2O | Secondary Circuit Settings | 0-25 | 5
0 | 1 | Secondary # | FGF PEEP |  |  | PEEPInt | Intrinsic PEEP from FGF |  | 4.80 | 4.20 | cmH2O | Secondary Circuit Calculated |  |  | Intrinsic PEEP (from FGF) Crude model: PEEPInt[i] = 0 if FGFtot[i] < 7LPM; 3 + (FGFtot[i] – 7)*0.6
1 | 1 | Secondary # | Total PEEP |  | 2.2.2 | APEEP | Actual PEEP at Patient Y |  | 14.80 | 14.20 | cmH2O | Secondary Circuit Calculated | 0-25 |  | APEEP[i] = PEEP0 + PEEPInt[i] + PEEP[i]
0 | 1 | Patient # | VCO2 |  | 3.2 | VCO2 | CO2 Production rate |  | 4.73 | 5.09 | ml/s | Patient Characteristics Calculated
0 | 0 |  |  |  |  | VO2 | Oxygen Consumption |  | 5.91 | 6.36 | ml/s | Patient Characteristics Calculated
0 | 0 |  |  |  | 3.1.1 | ADS | Anatomic Deadspace |  | 122.22 | 155.56 |  | Patient Characteristics Calculated
0 | 0 |  |  |  | 3.1.2 | CC | Secondary Circuit Compliance |  | 4.00 | 4.00 | ml/cmH2O | Secondary Circuit Settings |  |  | Can disregard. For 22 mm tubing the volume lost due to gas compression is approx 3.6 ml per cmH2O per cm Tubing
0 | 1 | Patient # | Alveolar VT |  | 3.1.3 | AVT | Alveolar Tidal Volume |  | 433.33 | 344.44 | ml | Patient Characteristics Calculated |  |  | Prev “VAP” = VT[i] – ( MIP[i]/CC ) - ADS[i]
1 | 1 | Patient # | PaO2 |  | 2.1.3 | PaO2 | Arterial partial pressure of Oxygen |  | 84.20 | 89.33 | mmHg | Patient Characteristics Calculated | 80-200
1 | 1 | Patient # | PaCO2 |  | 2.1.2 | PaCO2 | Arterial partial pressure of CO2 |  | 25.93 | 35.13 | mmHg | Patient Characteristics Calculated | 30-50
0 | 0 |  |  |  |  | CaCO2 | Arterial concentration of CO2 |  | 0.41 | 0.47 | ml/ml | Patient Characteristics Calculated
1 | 1 | Patient # | HCO3 | 1.0.; 2.0. Patient Characteristics | 2.1.4 | HCO3 | Arterial bicarbonate concentration |  | 24.00 | 24.00 | mM/L | Patient Characteristics Setting | 20-28 | 24
0 | 0 |  |  |  |  | [H+] | Arterial hydrogen ion concentration |  | 25.93 | 35.13 | nM/L | Patient Characteristics Calculated
1 | 1 | Patient # | pH |  | 2.1.1 | pH | Arterial blood acidity |  | 7.59 | 7.45 |  | Patient Characteristics Calculated | 7.3-7.4

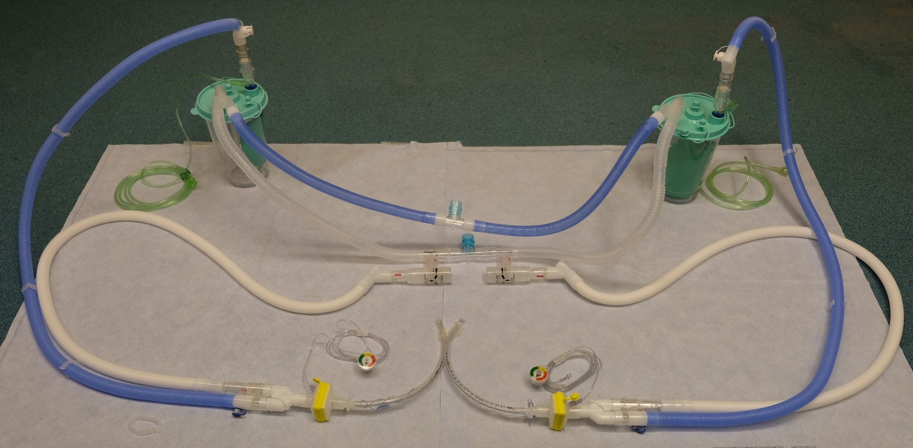
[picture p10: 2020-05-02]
docs/Image Sources/HospitalParts Instruction photos/CerebrusPhysicalSystem_HospitalParts.jpg

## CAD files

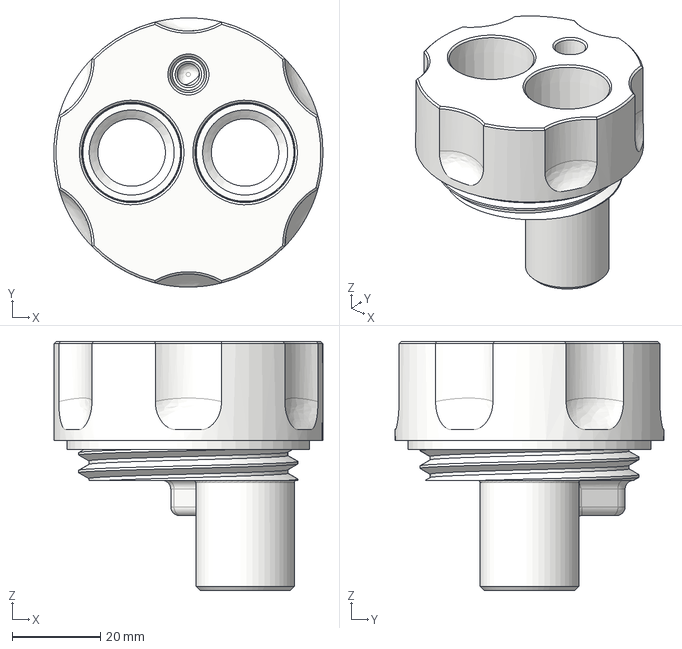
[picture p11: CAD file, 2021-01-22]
CAD Files/multivent_main_body.step
61.0 x 61.0 x 56.5 mm

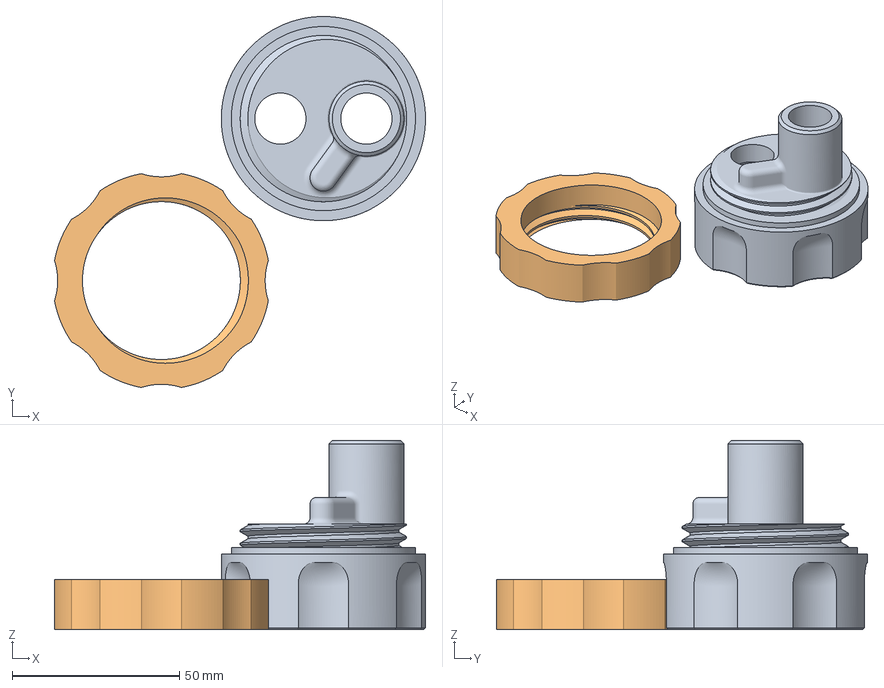
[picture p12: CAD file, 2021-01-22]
CAD Files/vent_splitter_concept_10_body.3mf
110.8 x 110.8 x 56.5 mm
vent_splitter_concept_10_body.stl
vent_splitter_concept_10_inner_cap.stl

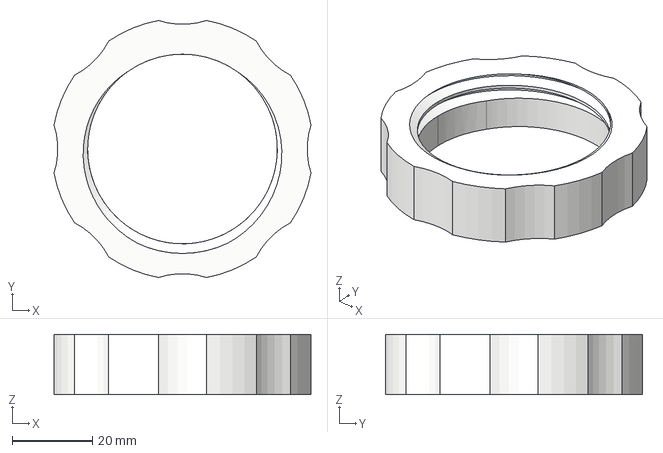
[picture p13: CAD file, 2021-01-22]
CAD Files/multivent_locking_cap.step
63.9 x 63.9 x 15.0 mm

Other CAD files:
CAD Files/multivent_locking_cap.stl
CAD Files/multivent_main_body.stl

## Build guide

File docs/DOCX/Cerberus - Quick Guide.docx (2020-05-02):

INITIALS SYSTEM SETUP – Driving Ventilator Settings
Step 1: | Ventilation Mode: Pressure Control
Step 2: | Driving Pressure = 60 m H20
Step 3: | Pressure limit = 75 cm H2O
Step 4: | Frequency/Respiratory Rate (RR) = 10 – 30 breathes per minute
Step 5: | Inspiratory time = 0.8 s (range = 0.6 – 1.0 s) I:E ratio = value needed to satisfy inspiratory time. - LOWER LIMIT = 1:2

Depending on the ventilator, inspiratory time may be separately set on the ventilator resulting in a defined I:E ratio for a given RR

OR

The I:E ratio is set resulting in a fixed inspiratory time for a given RR

Note that as RR increases, the I:E ratio must be decreased to maintain inspiratory time in appropriate range.

- For RR = 10. I:E = 1:6.5 in order to obtain an inspiratory time of 0.8 s
- For RR = 30. I:E = 1:2.33 in order to obtain an inspiratory time of 0.6 s

Step 6: | Rise Time = 50%
Step 7: | PEEP = 0
Step 8: | O2 = 21%
Step 9: | Flow Rate = 2 L/min
Step 10: | Volume Alarm = DISABLED - Note: Alarm is disabled at start-up for patient titration

After desired patient settings are titrated for each patient the VOLUME ALARM must be set as directed in “Alarms” instructions

Connecting Patient
Step 1: | Set Fresh gas flow = 4 L/min - 100% O2 or desired blended FiO2
Step 2: | Ensure each secondary circuit PEEP valve is set to 5 cm H20 - Confirm driving ventilator PEEP is set to 0 cm H2O
Step 3: | Connect patient to Cerebrus system via patient secondary circuit
Step 4: | Confirm peak inspiratory pressure on each manometer is no greater than clinically desired peak inspiratory pressure - Peak inspiratory pressure should be less than or equal to 35 cm H2O - If peak pressure exceeds clinically desired level, then fresh gas flow for the secondary patient circuit must be decreased to lower tidal volume until peak pressure is in desired range - Refer to instructions on “How to adjust tidal volume (for a given respiratory rate)”
Step 5: | Confirm the PEEP as indicated by the manometer is at least 5 cm H2O - Note: due to intrinsic PEEP generated by the ventilated patients fresh gas flow rate, measured PEEP will be 2-5 cm H2O above the set PEEP.
Step 6: | Titrate each ventilated patient to desired parameters
Step 7: | Observe ventilation for 2 minutes following titration of both patients to ensure steady state ventilation is reached
Step 8: | Set volume alarms as described in instructions on “Alarm Settings”

How to Adjust Tidal Volume (for a given respiratory rate)
Step 1: | Silence ventilator volume alarms
Step 2: | Ensure the inspiratory time on the driving ventilator is between 0.6 – 1.0 second - optimal = 0.8 seconds

Depending on the ventilator, inspiratory time may be separately set on the ventilator resulting in a defined I:E ratio for a given RR

OR

The I:E ratio is set resulting in a fixed inspiratory time for a given RR

I:E LOWER LIMIT = 1:2
Step 3: | Set desired tidal volume = Fresh Gas Flow Rate / Respiratory Rate - If set tidal volume results in peak inspiratory pressure greater than clinically desired peak inspiratory pressure then reduce fresh gas flow rate by 0.5 -1 L/min increments until clinically desired peak inspiratory pressure Fresh Gas Flow UPPER LIMIT = 14 L/min
Step 4: | Using inline manometer or spirometer, confirm the PEEP for the patient measures at desired level. - If not, adjust individual patient PEEP valve to desired level by following the instructions for “How to adjust patient PEEP” Note: due to intrinsic PEEP generated by the ventilated patients fresh gas flow rate, measured PEEP will be 2-5 cm H2O above the set PEEP.
Step 5: | Observe ventilation for 2 minutes following titration to ensure steady state ventilation is reached
Step 6: | Set volume alarms as described in instructions on “Alarm Settings”

How to Adjust Respiratory Rate
Step 1: | Reduce fresh gas flow rate on both secondary patient circuits to 4 L/min - This is done to ensure peak inspiratory pressures are not exceeded with a change in respiratory rate
Step 2: | Set respiratory rate to new desired rate on the driving ventilator
Step 3: | Set inspiratory time = 0.6 -1. S - Optimal = 0.8 s

Depending on the ventilator, inspiratory time may be separately set on the ventilator resulting in a defined I:E ratio for a given RR

OR

The I:E ratio is set resulting in a fixed inspiratory time for a given RR

I:E LOWER LIMIT = 1:2
Step 4: | Increase tidal volume to desired level according to instructions provided for “How to adjust tidal volume (for a given respiratory rate)”
Step 5: | Set volume alarms as described in instructions on “Alarm Settings”

How to Adjust Patient Specific PEEP

At higher fresh gas flow rates infer a clinically significant intrinsic PEEP to the system.
Step 1: | Determine the set value needed for the individual PEEP value
Step 2: | Clamp patient at endotracheal tube - This is done to preserve PEEP the patient currently has while the level is adjusted
| Volume alarms will trigger for inadequate volume return. This is expected and will resolve with reconnection of circuit after new PEEP target is set.
Step 3: | Disconnect secondary circuit patient expiratory limb between the proximal one-way valve and the PEEP valve

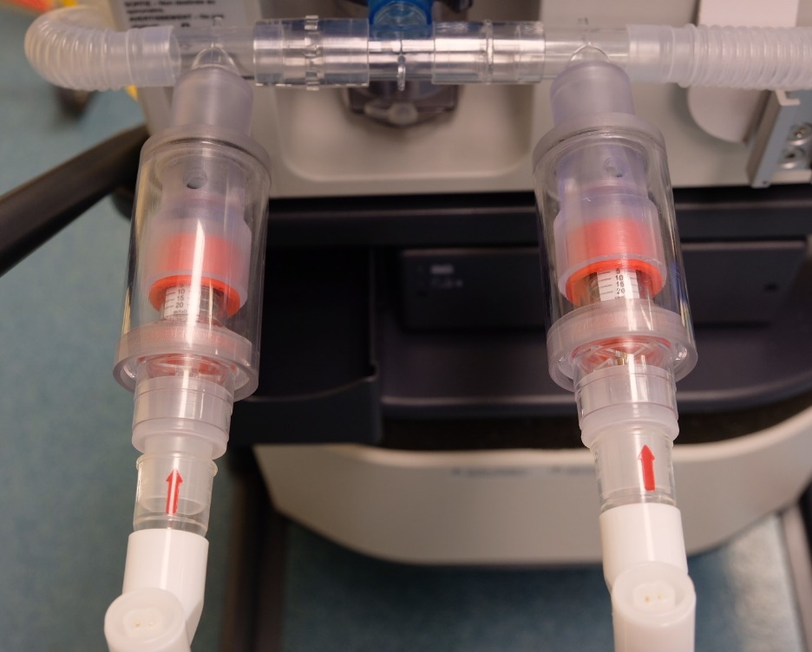
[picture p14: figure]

DISCONNECT HERE
Step 4: | Adjust PEEP valve to desired value. Prescribed value can be seen through the translucent external casing. - To adjust PEEP valve. Rotate the large diameter casing while valve casing is still connected to common expiratory limb tree of the driving ventilator - Increased PEEP = clockwise rotation - Decreased PEEP = counter clockwise rotation

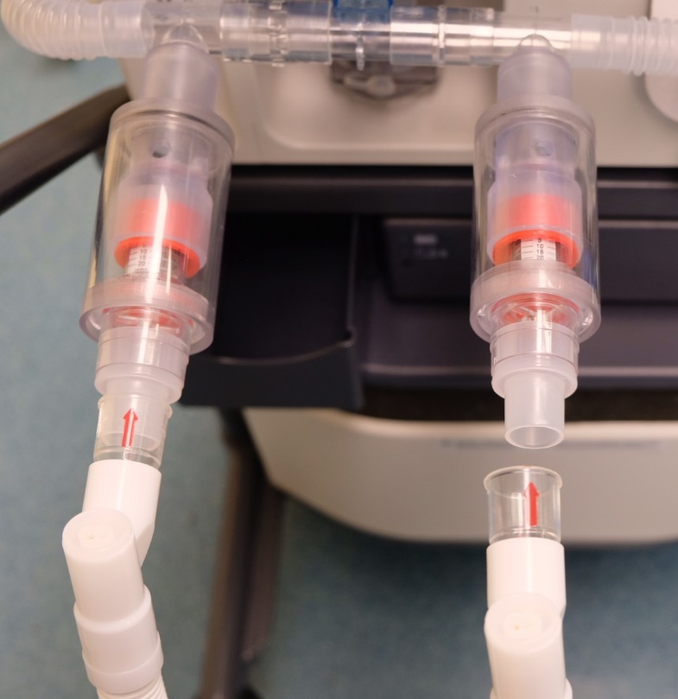
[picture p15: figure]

ROTATE HERE
Step 5: | Reconnect the secondary circuit patient expiratory limb to PEEP valve
Step 6: | Unclamp the endotracheal tube
Step 7: | Using manometer or spirometry, confirm that changes in PEEP has not resulted in peak inspiratory pressures greater than clinically desired peak inspiratory pressures - If peak inspiratory pressure exceeds clinically desired peak inspiratory pressure, decrease fresh gas flow in 1 L/min decrements until tidal volume decreases lower peak inspiratory pressures to desired thresholds. - Refer instructions provided for “How to adjust tidal volume (for a given respiratory rate)”
Step 8: | Using manometer or spirometry, confirm the PEEP is measured as desired patient individualized PEEP
Step 9: | Repeat steps 2-8 until desired PEEP is achieved
Step 10: | Observe ventilation for 2 minutes following titration to ensure steady state ventilation is reached
Step 11: | Set volume alarms as described in instructions on “Alarm Settings”

How to disconnect a patient from the Cerebrus System (while co-ventilated patient remains)
Step 1: | For patient to be disconnected, clamp ETT to maintain patient specific PEEP during transfer.

Volume alarm will trigger as it is correctly recognized as a disconnect
Step 2: | Using spirometry or observation of chest rise and breathing-delivery bag cycling, ensure the non-disconnected patients ventilation is unchanged.
Step 3: | Place disconnected patient onto one-to-one vent with desired setting for continued treatment
Step 4: | Place new patient on the Cerebrus System by following instructions for: 1. “Connecting Patient” 2. “How to adjust tidal volume (for a given respiratory rate)” 3. “How to adjust patient specific PEEP”
Step 5: | Observe ventilation for 2 minutes following titration to ensure steady state ventilation is reached
Step 6: | Set volume alarms as described in instructions on “Alarm Settings”

NOTE:

if only one patient is to remain on system then patient should be changed to normal ventilator tubing and initiated on one-to-one ventilation.

Alarm Settings

The volume alarm must be adjusted to appropriate levels following any changes in either co-ventilated patient’s ventilation parameters
Step 1: | Titrate each co-ventilated patient’s ventilation parameters as desired using instructions for: 1. “How to adjust tidal volume (for a given respiratory rate)” 2. “How t adjust respiratory rate” 3. “How to adjust patient specific PEEP”
Step 2: | Observe ventilation for 2 minutes following titration of both co-ventilated patient to ensure steady state ventilation is reached
Step 3: | Note the total volume returned to the ventilator as indicated on the monitors.
Step 4: | Set High Volume Alarm = “Total Volume Returned” + 100 mL
Step 5: | Set Low Volume Alarm = “Total Volume Returned” – 100 mL

Note

If pop-off valve is incorporated into secondary circuit patient expiratory limb then the above volume alarm settings will trigger for either secondary circuit disconnect or obstruction

Elevated Airway Pressure Monitoring (in the absence of pop-off valve in the patient secondary circuit expiratory limb)

- Requires ability to monitor pressure wave forms using a standard hemodynamic monitoring system
- DOES NOT provide true measure of inspiratory pressure. Refer to inline manometer for true inspiratory pressure

Step 1: | Set up arterial line transducer - NO fluid or pressure bag needed; leave IV spike end for IV bag OPEN to air - Zero art line transducer - Attach patient end of transducer to stopcock at HME filter

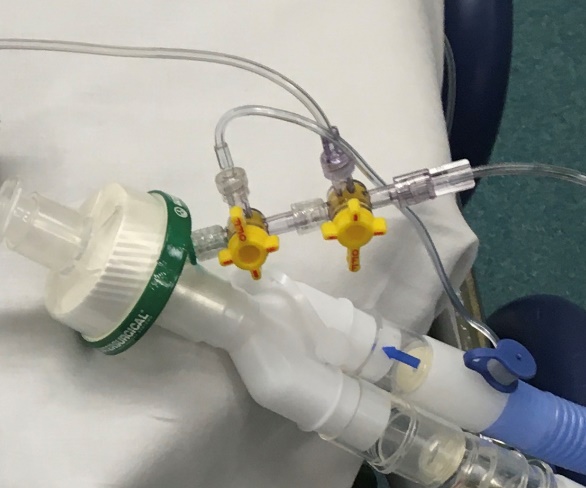
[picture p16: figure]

To arterial line transducer

PETCO2 stopcock

- Off in picture as not sampling continuously

To Inline manometer

Pressure stopcock for pressure monitoring
Step 2: | Set up pressure transducer on ICU monitor (Varies with make of monitor) I. Connect arterial line transducer to ICU monitor II. Select label with mean pressure ie: ICP III. Relabel “ICP” with “Ventilator” or tape and write ventilator pressure IV. DO NOT USE Arterial pressure labels. Ie. ART, FEM, ABP V. Suggested sweep speed = lowest sweep possible on monitor
Step 3: | Titrate each co-ventilated patient’s ventilation parameters as desired using instructions on: 1. “How to adjust tidal volume (for a given respiratory rate)” 2. “How t adjust respiratory rate” 3. “How to adjust patient specific PEEP”

Note: pressure tracing seen on monitor represents volume control ventilation (VCV)

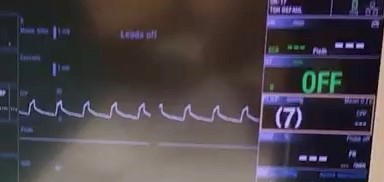
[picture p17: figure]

VCV

Waveform

Transduced mean pressure
Step 4: | Observe ventilation for 2 minutes following titration to ensure steady state ventilation is reached
Step 5: | Note the transduced mean pressure of the volume control wave form
Step 6: | Set the mean pressure alarm for the transduced pressure wave form to Mean Pressure (noted in Step 5) + 1 mm Hg

With the above settings, any increase in mean pressure resulting in alarm triggering OR change in waveform should prompt investigation of the patient for acute obstruction or dramatic increases in compliance.

- Immediate action = check peak inspiratory pressure using inline manometer

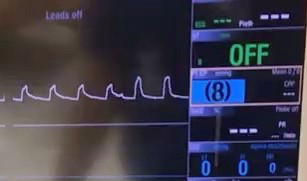
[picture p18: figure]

Increase in Mean Pressure

-Triggers alarm

Change in
pressure waveform

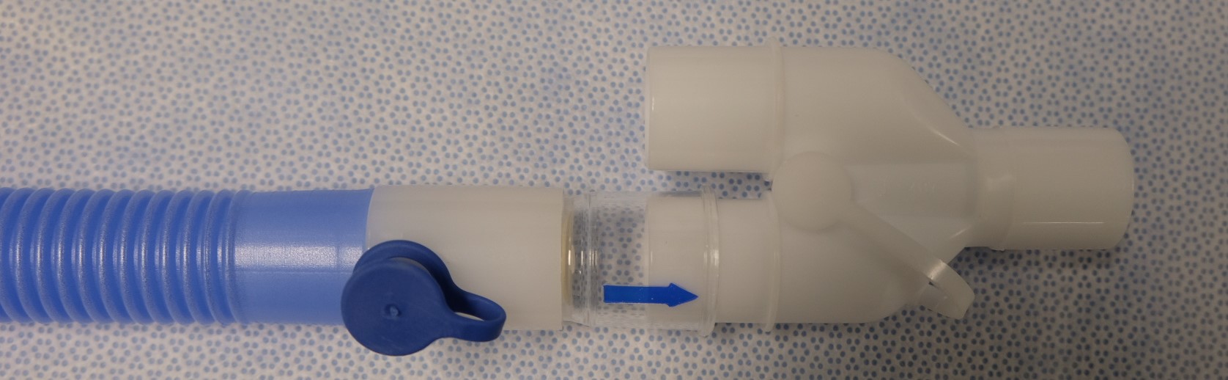
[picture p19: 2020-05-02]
docs/Image Sources/HospitalParts Instruction photos/Step21.jpg

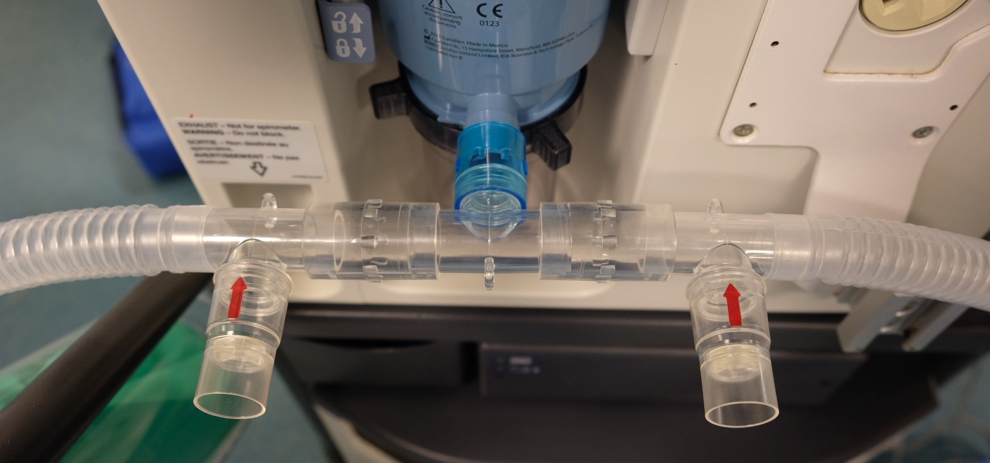
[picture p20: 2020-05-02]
docs/Image Sources/3D Instruction photos/Step8.jpg

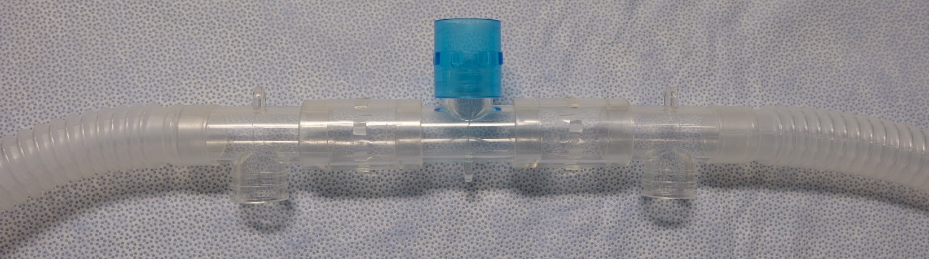
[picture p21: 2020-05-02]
docs/Image Sources/HospitalParts Instruction photos/Step6.jpg

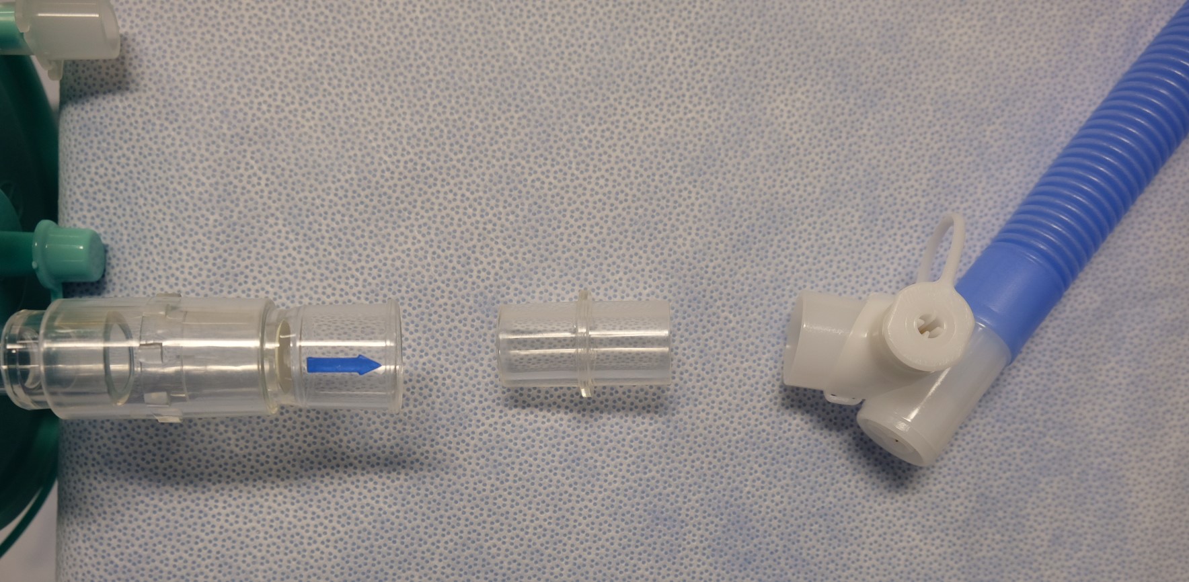
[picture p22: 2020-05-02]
docs/Image Sources/HospitalParts Instruction photos/Step19a.jpg

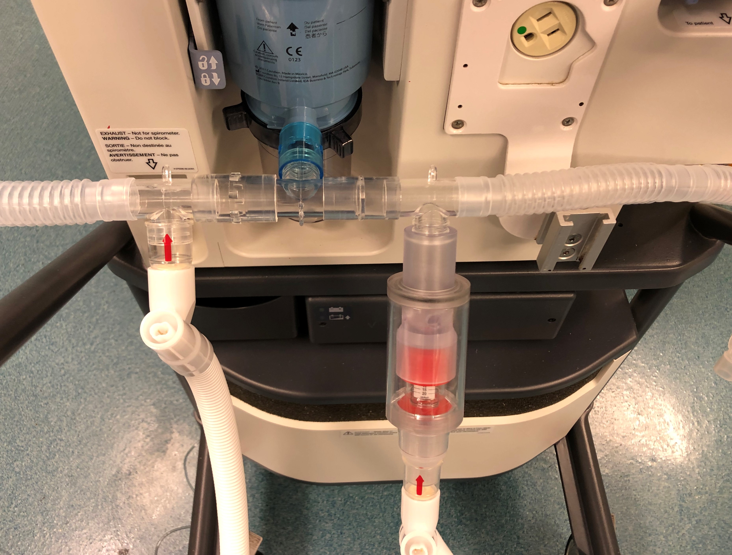
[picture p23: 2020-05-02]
docs/Image Sources/3D Instruction photos/PEEPinsertionB.jpg

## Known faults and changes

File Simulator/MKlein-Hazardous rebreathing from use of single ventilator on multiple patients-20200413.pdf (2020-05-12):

Michael Klein
232 Monarch Park Avenue
Toronto, Ontario, Canada M4J 4S1 michael@kleinonline.ca
416-575-8108

April 13, 2020

Prisma Health
701 Grove Road
Greenville, SC, USA 29605

To whom it may concern:
In response to the shortage of mechanical ventilators resulting from the global COVID-19 pandemic, several organizations have proposed or developed devices to ventilate two patients with one ventilator. Most of these devices involve flow-splitting adaptersthat are connected to the inspiratory and expiratory ports of the ventilator allowing for two patient breathing circuits to be connected to the ventilator simultaneously. I am writing to urgently inform you of a hazardous situation that may result from the use of these devices. A schematic of the ventilator configuration I am referring to is provided in Figure 1. Accessories such as monitors, humidifiers, and filters have been omitted for clarity.

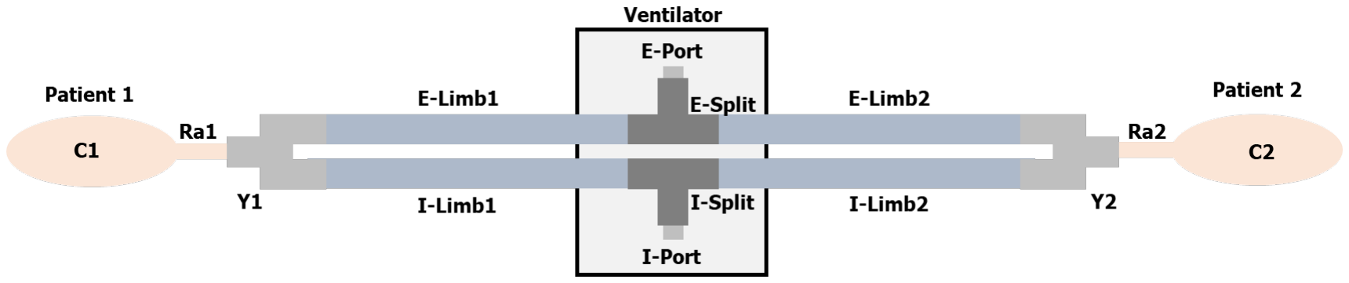
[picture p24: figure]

Figure 1: Schematic of ventilator configuration used to ventilate two patients with one ventilator. I-Port: Ventilator inspiratory port; E-Port: Ventilator expiratory port; I-Limb: Breathing circuit inspiratory limb; E-Limb: Breathing circuit expiratory limb; I-Split: Inspiratory flow splitting adapter; E-Split: Expiratory flow splitting adapter; Y: Patient wye piece; Ra: Airway resistance; C: Pulmonary compliance.
To adequately support a patient, a ventilator must meet two requirements. Firstly, the ventilator must deliver an adequate volume of gas to the patient’s lungs. Secondly, the majority of gas inspired into the lungs must be fresh gas from the ventilator and not gas that has already been inspired by the patient and expired back into the breathing circuit.
The configuration shown in Figure 1, if used with a pressure-controlled mode of ventilation, will provide volume delivery to each patient that is similar to the volume that would have been delivered if the patient were on the same ventilator alone, with the same settings, without the splitters. However, if the two patients do not have identical respiratory physiology (airway resistance and pulmonary compliance) or breathing circuits (tubing, filters, etc.) then the patients may inspire gas from the expiratory limbs of the breathing circuit and expire gas into the inspiratory limbs of the breathing circuits. As a result, expired gas, instead of fresh gas, may be reinspired during subsequent breaths. Expired gas has higher concentrations of carbon dioxide and lower concentrations of oxygen than fresh gas from the ventilator and, if rebreathed, may result in hypercapnia and/or hypoxia.

As a simple illustrative example, Figure 2 shows the flow of gas in the circuit if the connection to Patient 2 is fully occluded, which could occur due to a blocked airway filter, kinked endotracheal tube, or removal of Patient 2 from the ventilator and capping of the circuit.

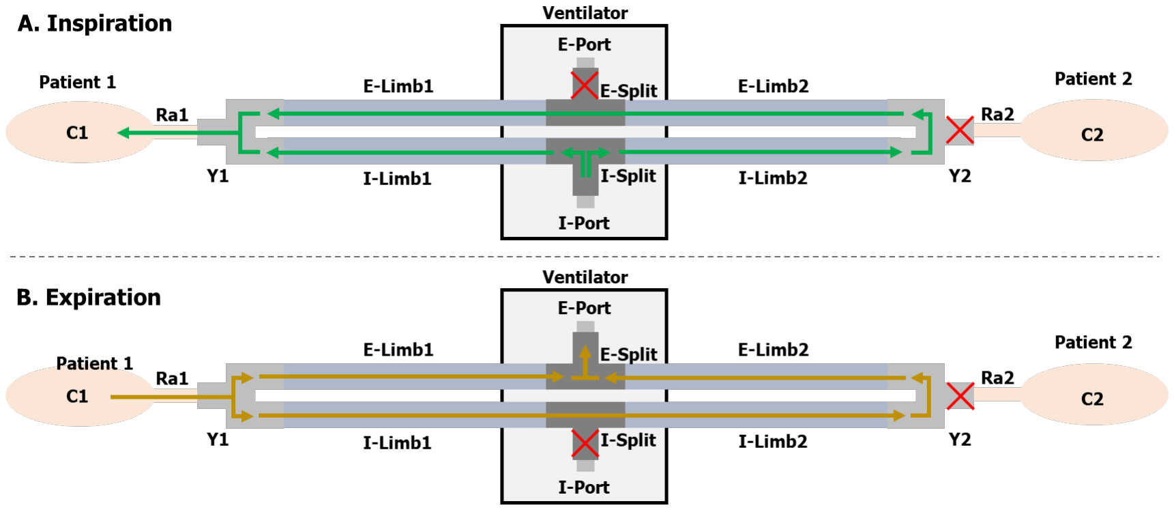
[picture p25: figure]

Figure 2: Flow of gas in the circuit when the connection to Patient 2 is fully occluded.
To demonstrate the effects of differing patient airway resistances, a computer simulation of the pneumatic circuit was executed. The parameters used for the simulation were a constant driving inspiratory pressure of 30 cmH2O, positive end expiratory pressure of 5 cmH2O, respiratory rate of 20 breaths/min, I:E ratio of 1:2, pulmonary compliance of 30 ml/cmH2O for both patients, a resistance of 2 cmH2O/L/s for all limbs of the breathing circuits, and an airway resistance of 10 cmH2O/L/s for Patient 1. The circuit was simulated for three values of Patient 2 airway resistance: A) 10 cmH2O/L/s to represent the situation where Patient 1 and 2 are identical, B) 20 cmH2O/L/s to represent the situation where the patients are not matched, and C) infinite resistance to simulate the situation where the airway is fully occluded or the circuit is capped (as in Figure 2). Circuit compliance and compressibility of gas were neglected for simplicity.
The resulting gas flows to Patient 1 in I-Limb1 and E-Limb1 are shown in Figure 3. As can be seen in Figure 3A, when the patients are identical, inspiratory gas is delivered to the patient exclusively via the inspiratory limb and expiratory gas exits the patient exclusively via the expiratory limb. However, when the airway resistance of Patient 2 is higher than that of Patient 1 (Figure 3B), some expired gas in E-Limb1 is delivered to Patient 1 during inspiration and, during expiration, some expiratory gas from Patient 1 flows into I-Limb1 and will be inspired in the next breath. If the connection to Patient 2 is fully occluded, the retrograde gas flow and resulting rebreathing becomes more severe (Figure 3C).

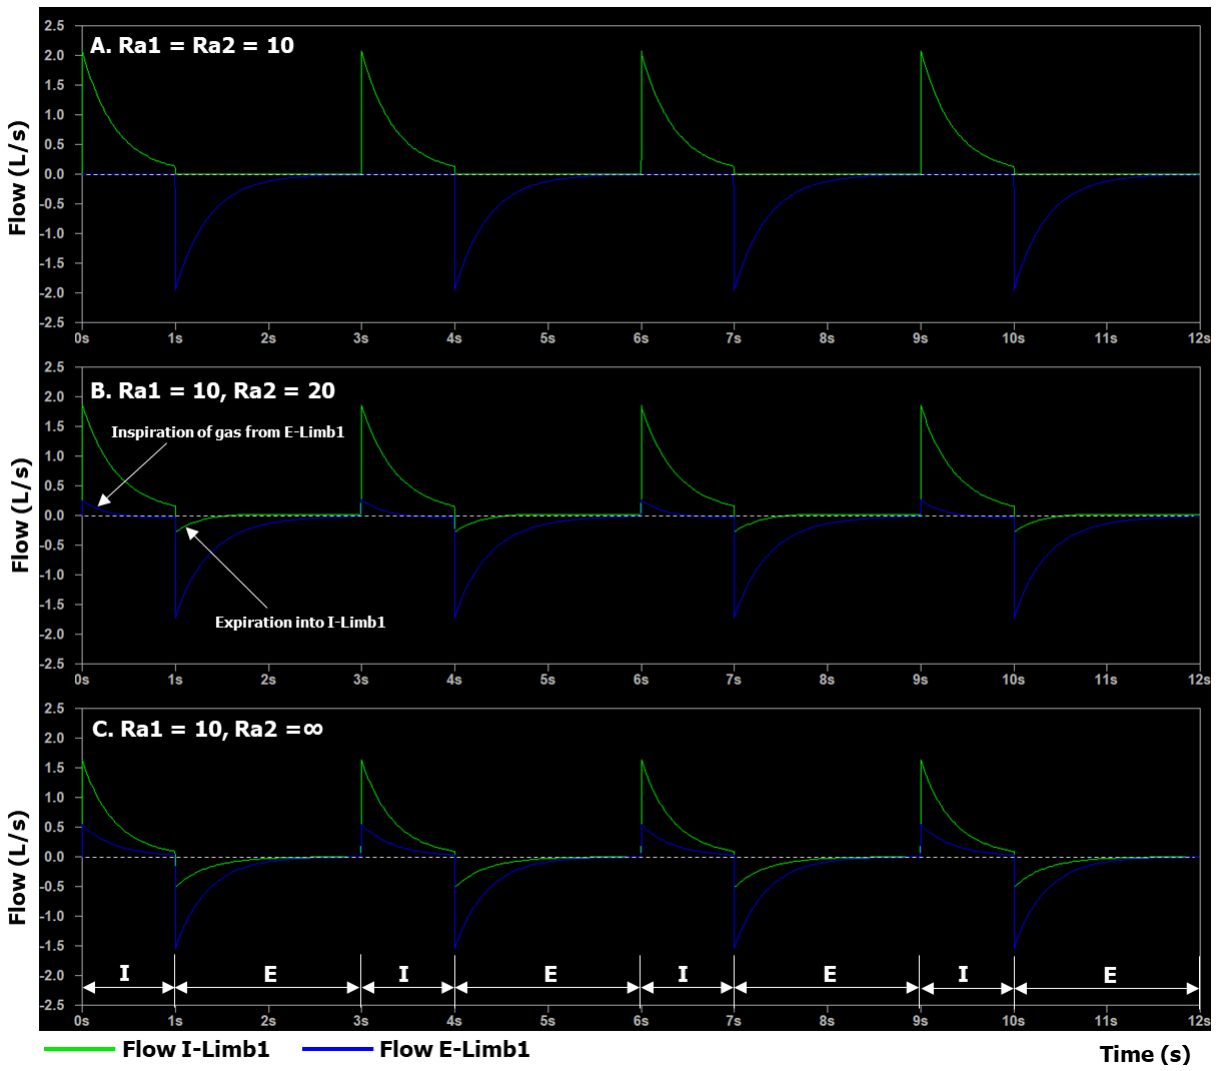
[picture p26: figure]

Figure 3: Flow to/from Patient 1 via I-Limb1 and E-limb1 when A) Patient 1 and Patient 2 have identical respiratory physiology; B) the airway resistance of Patient 2 is higher than Patient 1; and C) the connection to Patient 2 is fully occluded. Ra1: Airway resistance of Patient 1; Ra2: Airway resistance of Patient 2.
To demonstrate the effects of differing patient breathing circuit resistances, again, a computer simulation of the pneumatic circuit was executed. The parameters used for the simulation were a constant driving inspiratory pressure of 30 cmH2O, positive end expiratory pressure of 5 cmH2O, respiratory rate of 20 breaths/min, I:E ratio of 1:2, pulmonary compliance of 30 ml/cmH2O for both patients, an airway resistance of 10 cmH2O/L/s for both patients, and a resistance of 2 cmH2O/L/s for all limbs of the breathing circuits except E-Limb1. The circuit was simulated for three values of E-Limb1 resistance: A) 2 cmH2O/L/s to represent the situation where all limbs of the circuits are identical, B) 5 cmH2O/L/s to represent a small mismatch that may occur, for example, if an expiratory limb filter becomes damp or is a higher resistance model, and C) 15 cmH2O/L/s to simulate a highly obstructed limb as may occur with a clogged expiratory limb filter or kinked tube. Circuit compliance and compressibility of gas were neglected for simplicity.
The resulting gas flows to Patient 1 in I-Limb1 and E-Limb1 are shown in Figure 4. As can be seen in Figure 4A, when the circuits are identical, inspiratory gas is delivered to the patient exclusively via the inspiratory limb and expiratory gas exits the patient exclusively via the expiratory limb. However, when the expiratory limb resistance of Patient 1 is slightly higher than that of the other circuit limbs (Figure 4B), during expiration, some expiratory gas from Patient 1 flows into I-Limb1 and will be inspired in the next breath. If the expiratory limb of Patient 1 is highly obstructed, the expiratory flow of Patient 1 into I-Limb1 becomes more severe, exceeding the expiratory flow into E-Limb1 (Figure 4C).

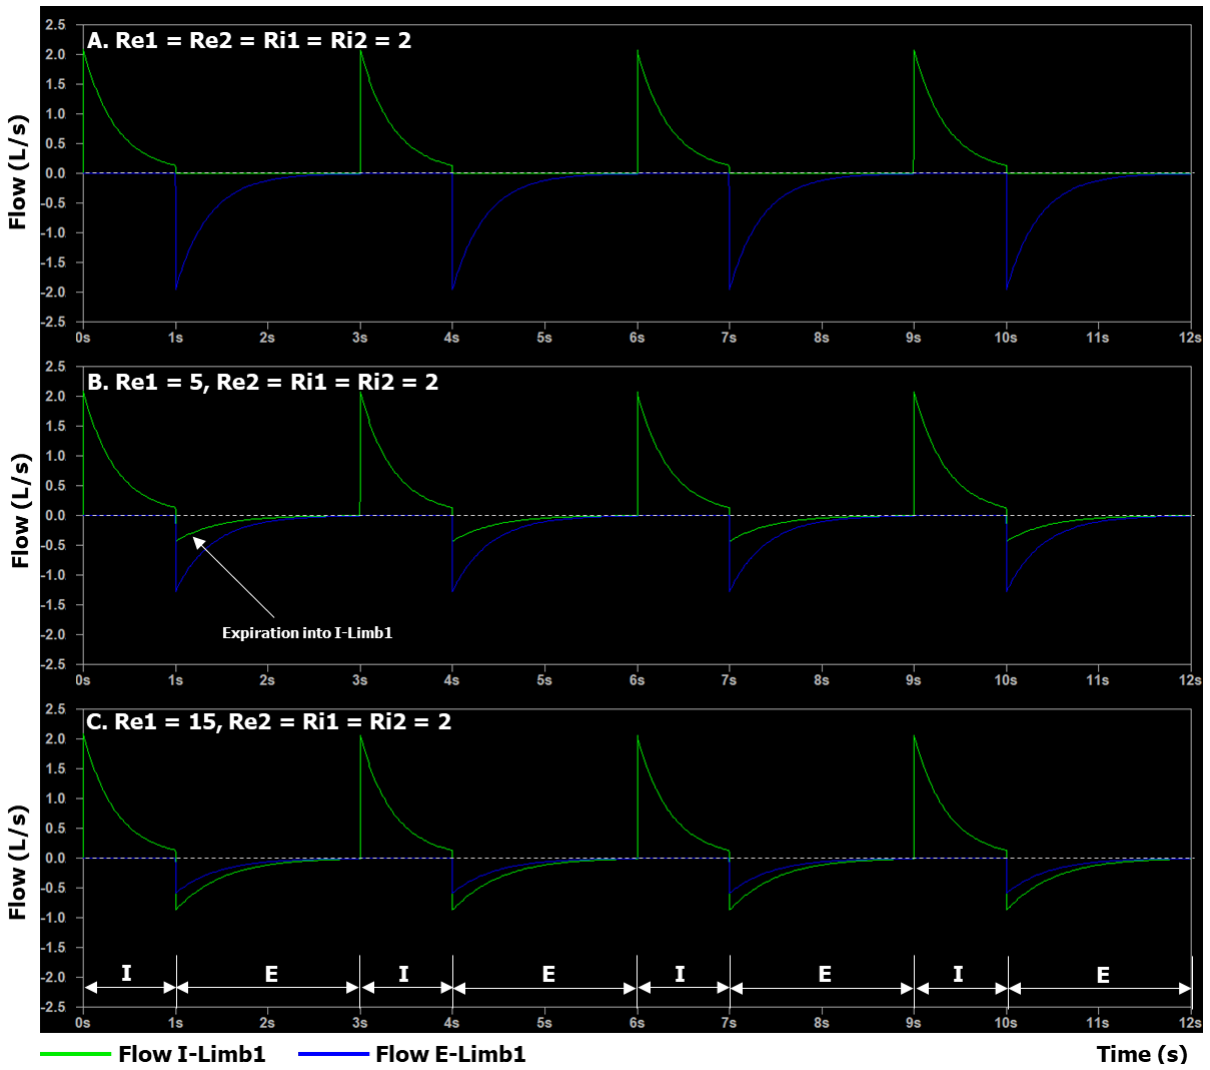
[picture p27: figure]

Figure 4: Flow to/from Patient 1 via I-Limb1 and E-limb1 when A) Patient 1 and Patient 2 have identical expiratory limb resistances; B) the expiratory limb resistance of Patient 1 is slightly higher than the other limbs of the breathing circuits; and C) the expiratory limb of Patient 1 is highly obstructed. Re1: Resistance of Patient 1 expiratory limb; Re2: Resistance of Patient 2 expiratory limb; Ri1: Resistance of Patient 1 inspiratory limb; Ri2: Resistance of Patient 2 inspiratory limb.
In order to prevent this potentially hazardous rebreathing, the patient connection ports of the flow-splitting adapters should be fitted with low-resistance respiratory check valves, as shown by the green boxes with blue arrows in Figure 5. Examples of such valves are produced by Qosina (https://www.qosina.com/) under part numbers 97351 and 97352.

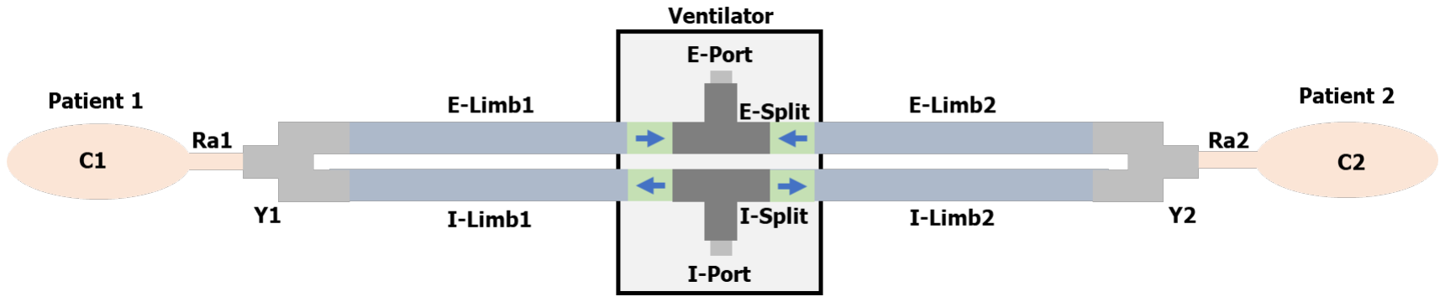
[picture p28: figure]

Figure 5: Schematic of ventilator configuration used to ventilate two patients with check valves to prevent rebreathing.
To demonstrate the effect of these check valves, the worst-case conditions of Figure 3C and Figure 4C were simulated again with the addition of check valves to the circuit. The results are shown in Figure 6A and Figure 6B, respectively. These results demonstrate that, with the addition of check valves, inspiratory gas is delivered to the patient exclusively via the inspiratory limb, expiratory gas exits the patient exclusively via the expiratory limb, and no rebreathing occurs, even when the patients and/or breathing circuits are highly mismatched.

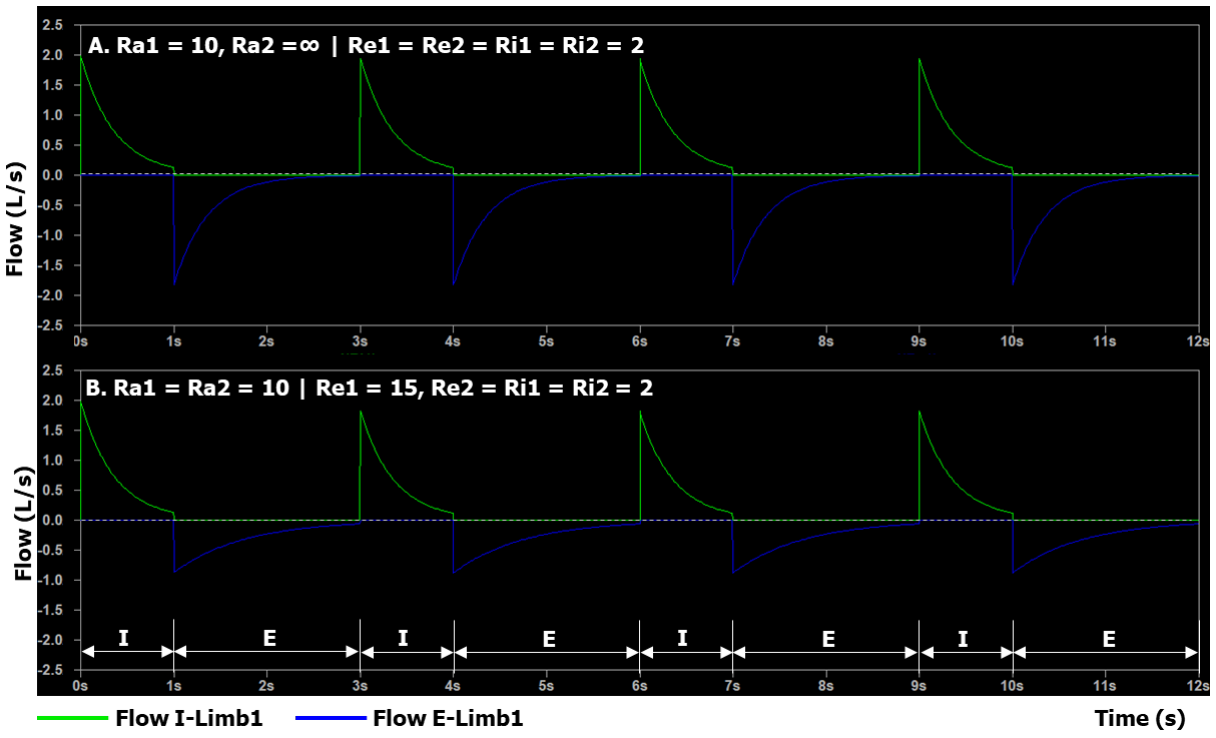
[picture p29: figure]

Figure 6: Simulation results of mismatched patients and circuits with the addition of check valves to the circuit. Ra1: Airway resistance of Patient 1; Ra2: Airway resistance of Patient 2; Re1: Resistance of Patient 1 expiratory limb; Re2: Resistance of Patient 2 expiratory limb; Ri1: Resistance of Patient 1 inspiratory limb; Ri2: Resistance of Patient 2 inspiratory limb.
I hope that you will carefully consider the information provided and take all appropriate actions to mitigate the identified risks. Please do not hesitate to contact me with any questions.
Sincerely,

Michael Klein, BASc, MSc

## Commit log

2020-06-07 Add simulator code.
    [spreadsheet.csv]
2021-01-22 added CAD files
    [multivent_locking_cap.step, multivent_locking_cap.stl, multivent_main_body.step, multivent_main_body.stl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]
